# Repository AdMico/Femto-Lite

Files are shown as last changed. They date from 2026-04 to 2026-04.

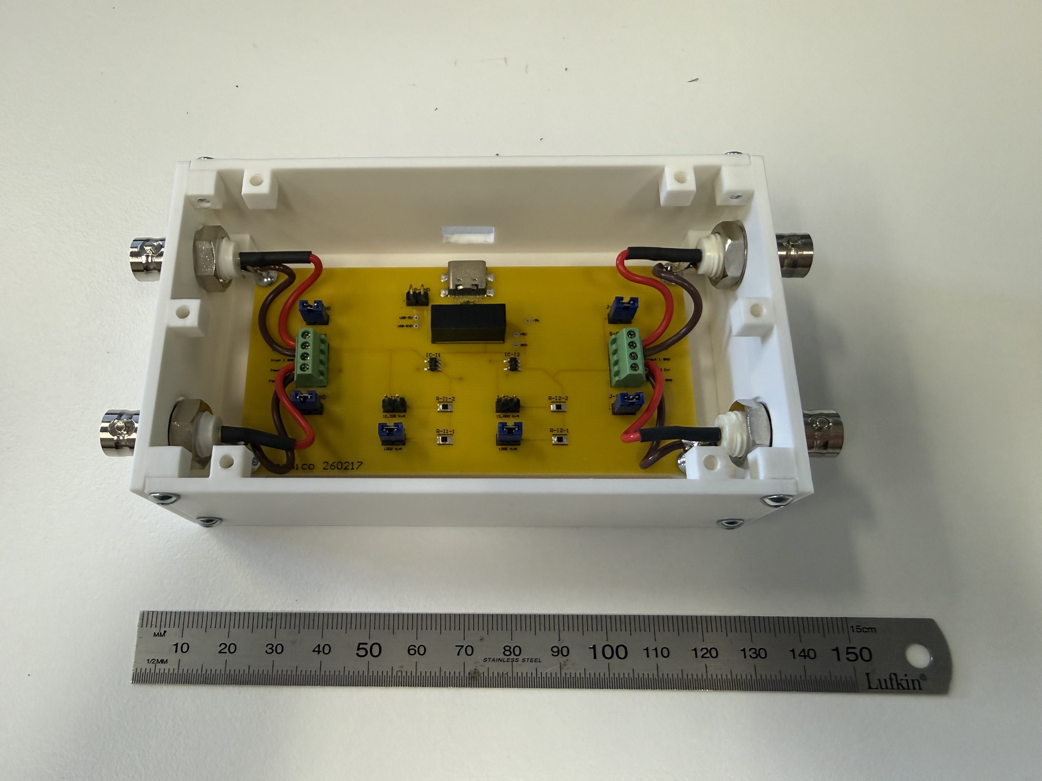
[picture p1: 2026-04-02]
PCBs & Schematics/Femto-Lite Assembled 2.jpeg

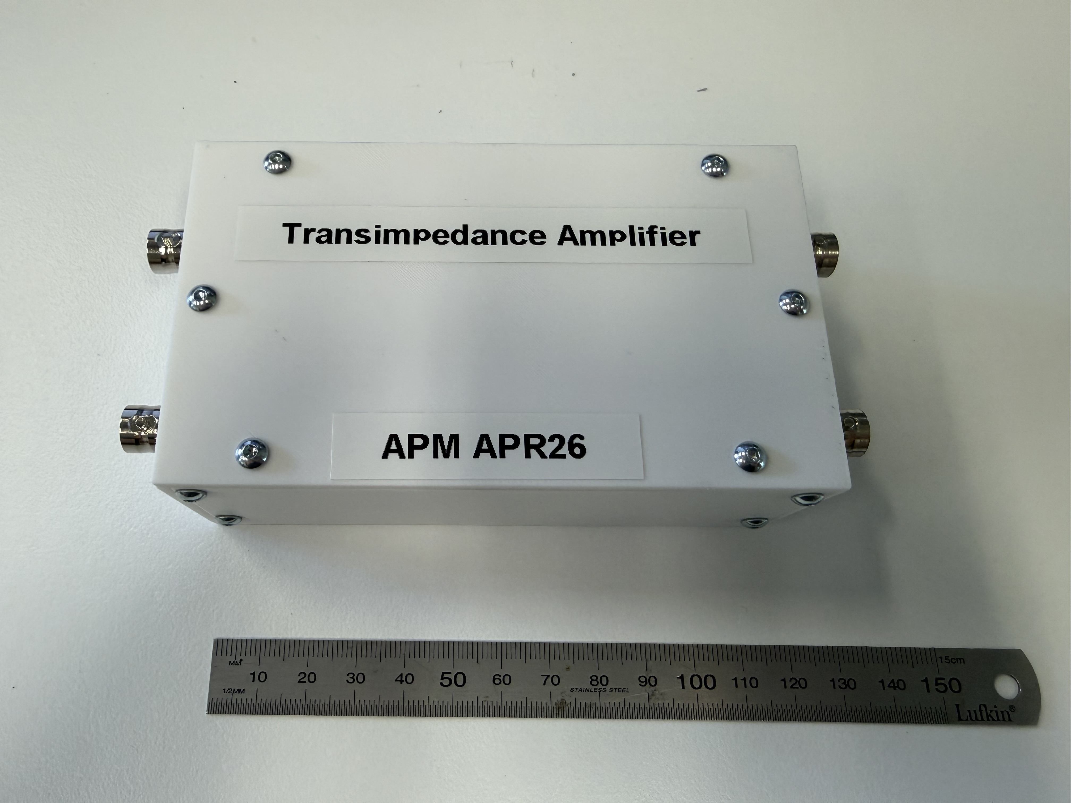
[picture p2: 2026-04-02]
PCBs & Schematics/Femto-Lite Assembled 1.jpeg

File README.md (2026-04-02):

# Femto-Lite v1.0.0 (Updated 02APR26 APM)

**Written by:** Adam Micolich

**Purpose:** Design aspects for a low-cost USB-C powered two-channel transimpedance amplifier with two gain settings (1000V/A and 10000V/A).

## Structure

The top level has three folders -- *CNC Parts*, *3D Print Parts* and *PCBs & Schematics*.

The *CNC Parts* folder contains CNC-ready files for producing all the panels for the Femto-lite box in metal.

The *3D Print Parts* folder contains 3D print-ready files for producing all the panels for the Femto-lite box in plastic.

The *PCBs & Schematics* folder contains the PCB design, Schematic and the Gerber file set for production for the PCB used in this project. It also contains a parts list for all the additional components required, along with some photographs and test data.

Each of the three folders above has its own `README.md` file with further details regarding the contents of those folders.

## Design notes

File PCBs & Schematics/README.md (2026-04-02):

# Femto-Lite v1.0.0 (Updated 02APR26 APM)

**Written by:** Adam Micolich

## Contents of the *PCBs & Schematics* folder

There is a single PCB in the Femto-Lite. The various files and folders are as follows:

`Femto-Lite Schematic.pdf`: The schematic diagram for the circuit used in this box.

`Femto-Lite PCB Design.pdf`: PCB design shown to actual size.

`Femto-Lite Parts List.pdf`: Parts list for all the components needed for assembly.

`Femto-Lite Assembled 1.jpeg`: Photograph of an assembled Femto-Lite with top panel in place.

`Femto-Lite Assembled 2.jpeg`: Photograph of an assembled Femto-Lite with top panel removed.

`Femto-Lite Specs.pdf`: Plots of output voltage vs input current for the two gain settings 1000V/A and 10000V/A.

*Gerber Files*: A folder containing all the Gerber files needed to have these PCBs produced. It is a fairly standard two-layer PCB.

We get these PCBs made for us by PCBWay in China.

## Brief discussion of the circuit design aspects for the Femto-Lite

The Femto DLPCA-200 current pre-amplifier has long been used in electrical measurement setups at UNSW, often for measuring current signals that simply don't require the performance (and the price it entails) provided by the DLPCA-200. This instrument was designed to provide a simple, low-cost two-channel equivalent of a Femto DLPCA-200 for the measurement of d.c. and quasi-d.c. currents in the mA to high uA range.

The circuit centres on a traditional transimpedance amplifier circuit using the Texas Instruments TLV2721 Op-amp. The circuit is designed with two gain settings 1000 V/A and 10000 V/A that can be switched between using jumpers. Notionally, other gains could be obtained simply by replacing the feedback resistors on the op-amp, which are simply precision 0805 SMT resistors.

The circuit is powered using a USB-C power supply, which is fed into an isolated dc-dc converter to provide +/-5V rails for the op-amp, such that the amplifier can work bipolar rather than unipolar. As such, the voltage outputs saturate at around 5V -- there is no overload circuitry in order to keep costs down, so a user needs to be cognizant of ensuring the input signal does not become to high. Breaking the circuit is unlikely unless the current overload is severe, the measurement will just be 'clipped'.

The remaining jumpers are provided for grounding versatility (e.g., noise optimisation). There are two banks of screw-terminals on the board for the BNC connections -- note that each of these appears twice in the schematic to enable the connections to be properly mapped, the BNC connections come in at the screw-points, the circuit connections are the solder pins, respectively.

The circuit behaves with good linearity to almost zero input current. Note that the output voltage is the opposite sign of the input current, an inherent aspect of the transimpedance amplifier, where V_out = -I_in/R_F where R_F is the feedback resistance.

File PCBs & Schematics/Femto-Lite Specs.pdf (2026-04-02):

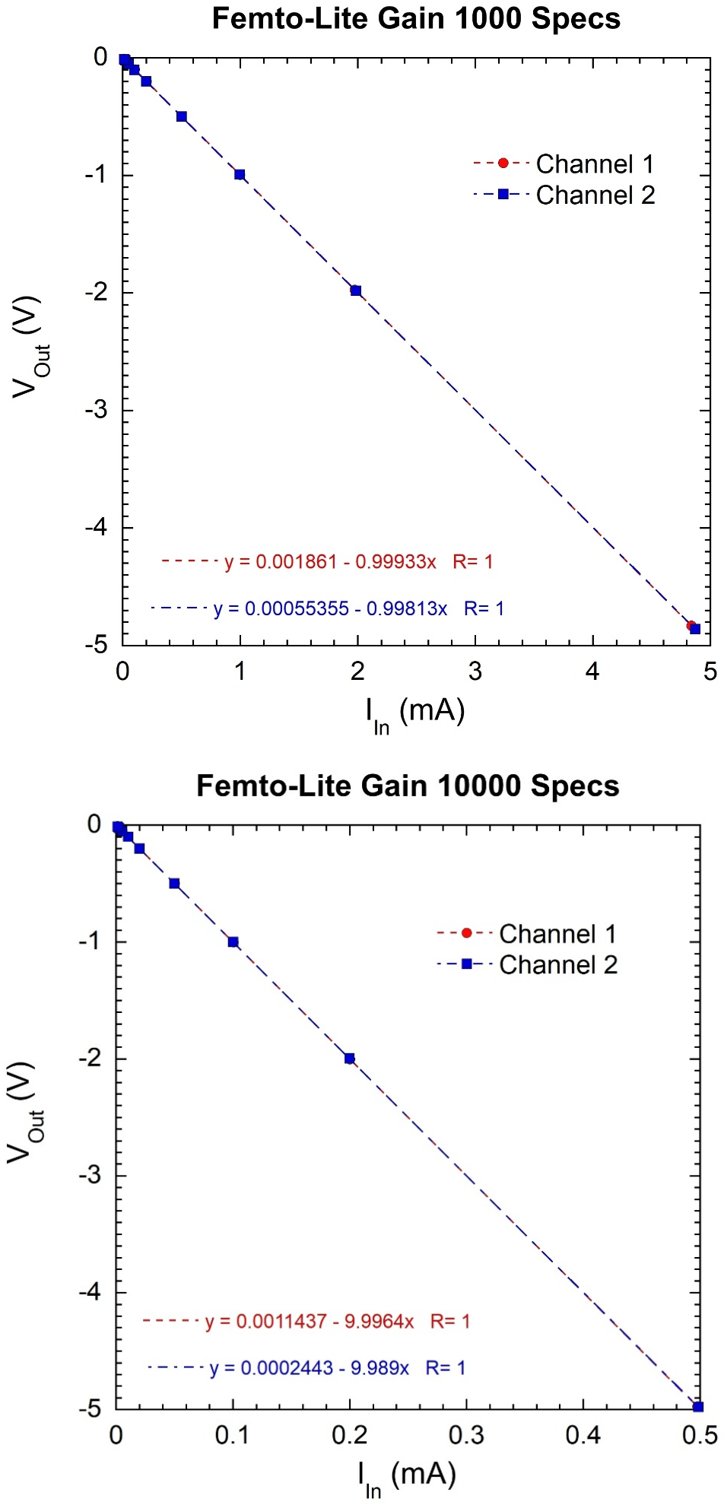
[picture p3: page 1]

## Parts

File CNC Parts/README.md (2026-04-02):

# Femto-Lite v1.0.0 (Updated 02APR26 APM)

**Written by:** Adam Micolich

## Contents of the *CNC Parts* folder

This folder has CNC-ready STEP files for all the various panels of the box. The various files are as follows:

`Femto-Lite_Back_V1-Body.step`: This makes the rear wall of the Femto-Lite box, which supports the access port for the USB-C power supply.

`Femto-Lite_Bottom_V1-Body.step`: This makes the baseplate of the Femto-Lite box, with screwpoints for mounting the Femto-Lite PCB.

`Femto-Lite_Front_V1-Body.step`: This makes the front wall of the Femto-Lite box, which is a clean panel.

`Femto-Lite_LeftSide_V1-Body.step`: This makes the left wall of the Femto-Lite box, which supports the two input BNC connectors.

`Femto-Lite_RightSide_V1-Body.step`: This makes the right wall of the Femto-Lite box, which supports the two output BNC connectors.

`Femto-Lite_Top_V1-Body.step`: This makes the top lid panel of the Femto-Lite box.

The panels are designed to be machined in aluminium, which is then bead-blasted and anodised, and can be readily done via a company such as PCBway or JLCPCB. I tend to hand-tap the threaded holes myself, both to reduce the CNC cost and ensure the threads are done well.

Any holes in these panels will either be drilled to 3mm diameter, and be clearance holes for an M3 bolt, or be drilled to 2.5mm diameter, ready to be tapped to M3 as a threaded hole for an M3 bolt. It is easy to check which is which using an M3 bolt. ;)

A photographs of a fully assembled Femto-Lite can be found in the *PCBs & Schematics* folder.

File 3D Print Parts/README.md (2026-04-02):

# Femto-Lite v1.0.0 (Updated 02APR26 APM)

**Written by:** Adam Micolich

## Contents of the *3D Print Parts* folder

This folder has print-ready STL files for all the various panels of the box. The various files are as follows:

`Femto-Lite_Back_V1-Body.stl`: This makes the rear wall of the Femto-Lite box, which supports the access port for the USB-C power supply.

`Femto-Lite_Bottom_V1-Body.stl`: This makes the baseplate of the Femto-Lite box, with screwpoints for mounting the Femto-Lite PCB.

`Femto-Lite_Front_V1-Body.stl`: This makes the front wall of the Femto-Lite box, which is a clean panel.

`Femto-Lite_LeftSide_V1-Body.stl`: This makes the left wall of the Femto-Lite box, which supports the two input BNC connectors.

`Femto-Lite_RightSide_V1-Body.stl`: This makes the right wall of the Femto-Lite box, which supports the two output BNC connectors.

`Femto-Lite_Top_V1-Body.stl`: This makes the top lid panel of the Femto-Lite box.

The panels are designed to be 3D printed. I hand-tap the threaded holes myself, since threads can't be reliably printed.

Any holes in these panels will either be printed to 3mm diameter, and be clearance holes for an M3 bolt, or be printed to 2.5mm diameter, ready to be tapped to M3 as a threaded hole for an M3 bolt. It is easy to check which is which using an M3 bolt. ;)

A photographs of a fully assembled Femto-Lite can be found in the *PCBs & Schematics* folder.

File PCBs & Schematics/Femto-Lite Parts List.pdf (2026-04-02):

Part | Part Number | Manufacturer | Supplier | Qty | Cost | Subtotal

Main Board

2-pin Jumper Pins | G800NA306018EU | Amphenol | Mouser | 9 | $0.160 | $1.44
2-pin Jumper Connectors | 60900213621 | Wurth Elektronik | Mouser | 9 | $0.496 | $4.46
USB-C PCB Connector | USB4110-GF-A | GCT | Mouser | 1 | $2.130 | $2.13
BNC 50ohm Bulkhead Connector | CONBNC004 | TE Connectivity | Mouser | 4 | $3.500 | $14.00
4-pin Terminal Block | TBC05-04-1-G-G | GCT | Mouser | 2 | $1.760 | $3.52
5V DC/DC Converter | NKA0505SC | Murata | Mouser | 1 | $13.380 | $13.38
10Kohm 0.05% Resistor | ERA-6VRW1002V | Panasonic | Mouser | 2 | $0.736 | $1.47
1Kohm 0.05% Resistor | ERA-6VRW1001V | Panasonic | Mouser | 2 | $0.736 | $1.47
Operational Amplifier | TLV2721CDBVR | Texas Instruments | Mouser | 2 | $2.000 | $4.00
| | | | | TOTAL | $45.88
Prices at 19/2/26

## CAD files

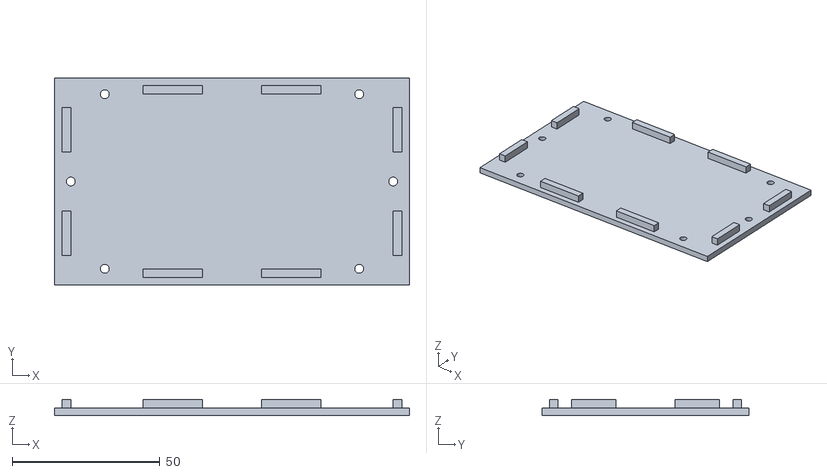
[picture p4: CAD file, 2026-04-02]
3D Print Parts/Femto-Lite_Top_V1-Body.stl
120.0 x 70.0 x 5.50

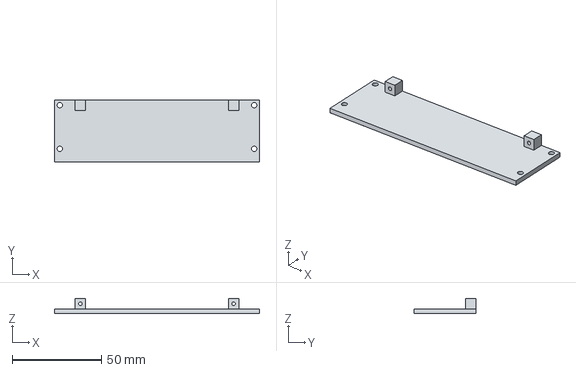
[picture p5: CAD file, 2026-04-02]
CNC Parts/Femto-Lite_Front_V1-Body.step
115.0 x 35.0 x 8.50 mm

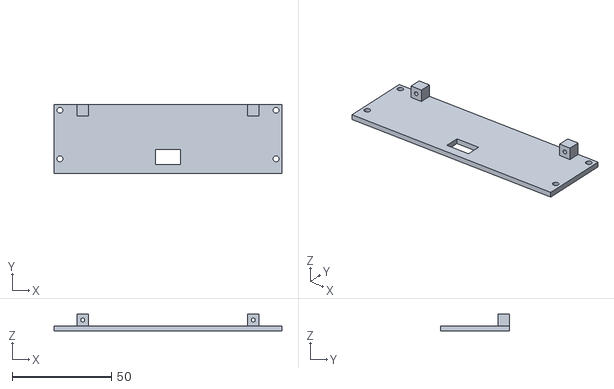
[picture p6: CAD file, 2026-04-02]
3D Print Parts/Femto-Lite_Back_V1-Body.stl
115.0 x 35.0 x 8.50

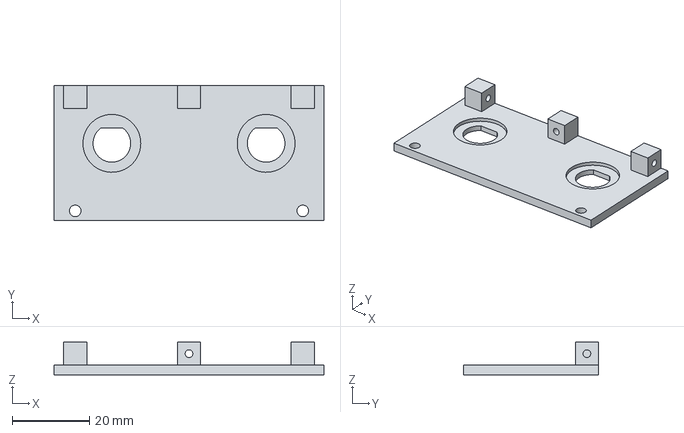
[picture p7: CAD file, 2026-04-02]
CNC Parts/Femto-Lite_RightSide_V1-Body.step
70.0 x 35.0 x 8.50 mm

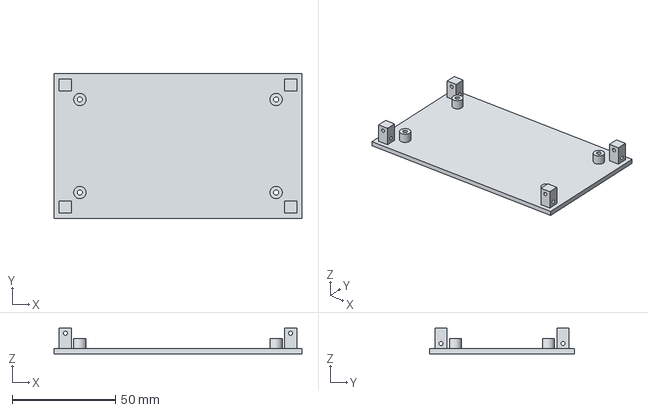
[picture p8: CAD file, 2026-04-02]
CNC Parts/Femto-Lite_Bottom_V1-Body.step
120.0 x 70.0 x 12.5 mm

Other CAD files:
3D Print Parts/Femto-Lite_RightSide_V1-Body.stl
3D Print Parts/Femto-Lite_LeftSide_V1-Body.stl
CNC Parts/Femto-Lite_Top_V1-Body.step
3D Print Parts/Femto-Lite_Front_V1-Body.stl
CNC Parts/Femto-Lite_Back_V1-Body.step
3D Print Parts/Femto-Lite_Bottom_V1-Body.stl

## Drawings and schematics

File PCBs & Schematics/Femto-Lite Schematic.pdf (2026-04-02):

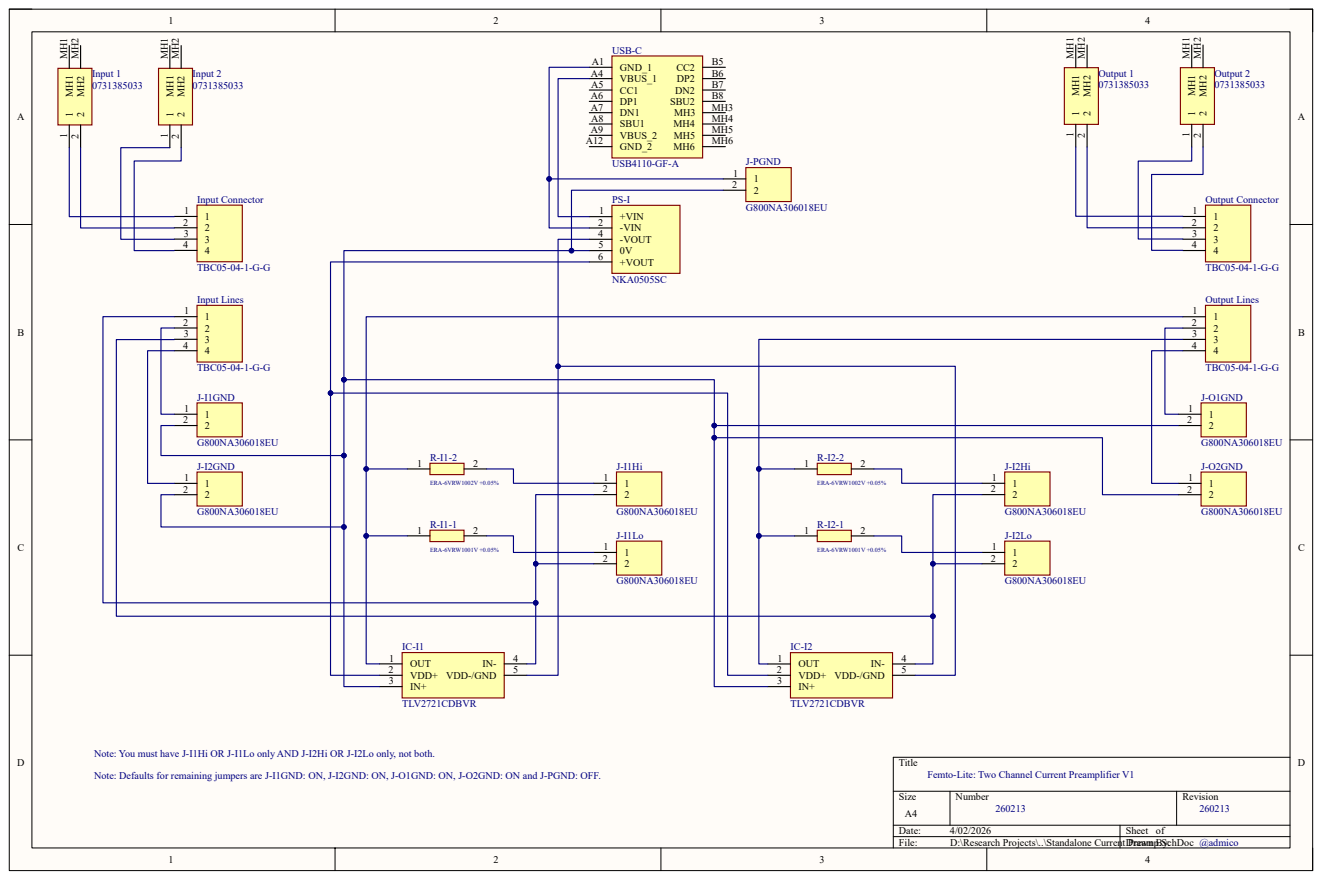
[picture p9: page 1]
Input Connector; TBC05-04-1-G-G; +VIN 1 -VIN 2 -VOUT 4 0V 5 +VOUT 6; NKA0505SC; OUT 1 VDD+ 2 IN+ 3; VDD-/GND; TLV2721CDBVR; ERA-6VRW1001V +0.05%; ERA-6VRW1002V +0.05%; J-I2GND; J-I1GND; Input Lines; Output Connector; Output Lines; GND_1 A1 VBUS_1 A4 CC1 A5 DP1 A6 DN1 A7 SBU1 A8 VBUS_2 A9 GND_2 A12; SBU2; USB-C; USB4110-GF-A; 2 MH1 MH1 MH2 MH2 Input 1 0731385033; 2 MH1 MH1 MH2 MH2 Input 2 0731385033; 2 MH1 MH1 MH2 MH2 Output 1 0731385033; 2 MH1 MH1 MH2 MH2 Output 2 0731385033; J-O1GND; J-O2GND

J-PGND

Note: You must have J-I1Hi OR J-I1Lo only AND J-I2Hi OR J-I2Lo only, not both.

Title
Femto-Lite: Two Channel Current Preamplifier V1

Note: Defaults for remaining jumpers are J-I1GND: ON, J-I2GND: ON, J-O1GND: ON, J-O2GND: ON and J-PGND: OFF.

Size A4 | Number 260213 | Revision 260213

Date: 4/02/2026 | Sheet of
File: D:\Research Projects\..\Standalone Current Preamp.SchDoc Drawn By: | @admico

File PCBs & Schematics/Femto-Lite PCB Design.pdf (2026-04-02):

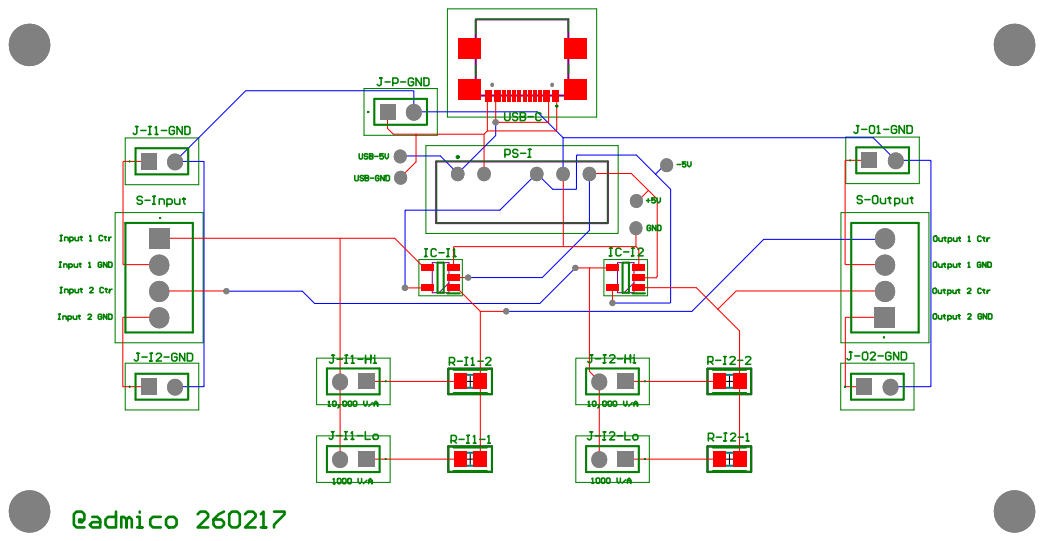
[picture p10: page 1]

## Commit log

2026-04-02 Initial Upload
    [Femto-Lite_Bottom_3D_Body.gbr, Femto-Lite_Bottom_Assembly.gbr, Femto-Lite_Bottom_Component_Center.gbr, Femto-Lite_Bottom_Courtyard.gbr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]
2026-04-02 Update Files
    [Femto-Lite_Back_V1-Body.step, Femto-Lite_Back_V1-Body.stl, Femto-Lite_Bottom_V1-Body.step, Femto-Lite_Bottom_V1-Body.stl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]
